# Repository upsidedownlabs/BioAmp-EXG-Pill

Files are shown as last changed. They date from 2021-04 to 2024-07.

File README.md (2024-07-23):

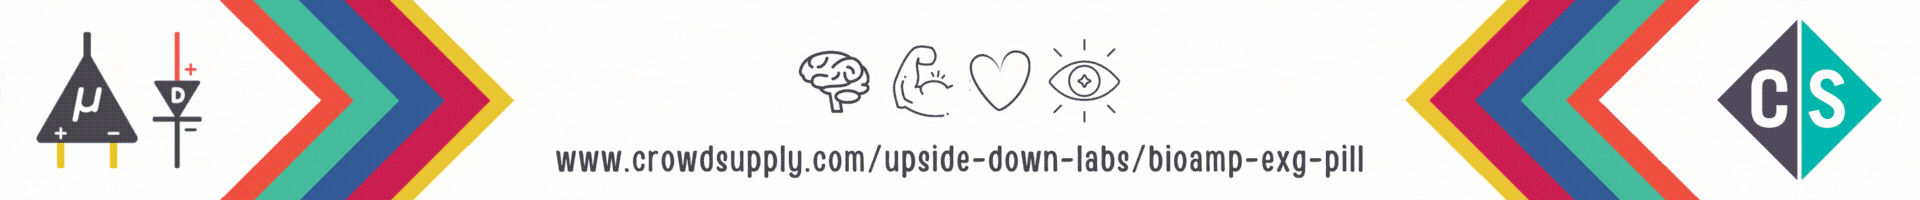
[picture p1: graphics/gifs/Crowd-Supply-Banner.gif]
Down Labs BioAmp EXG Pill Crowd Supply banner (https://www.crowdsupply.com/upside-down-labs/bioamp-exg-pill)


    

BioAmp EXG Pill is a small (2.54 X 1.00 cm) and elegant Analog Front End (AFE) board for BioPotential signal acquisition that you can use with any 5v Micro Controller Unit (MCU) with an ADC. It is capable of recording publication grade BioPotential signals like ECG, EMG, EOG, and EEG without the inclusion of any dedicated Hardware/Software filter, see [BioAmp EXG Pill v0.7 intro video](https://www.youtube.com/watch?v=-G3z9fvQnuw) for more info. The v1.0 of BioAmp EXG pill provides even more flexibilty with configuration option for Gain, BandPass, Filter, and Electrodes.

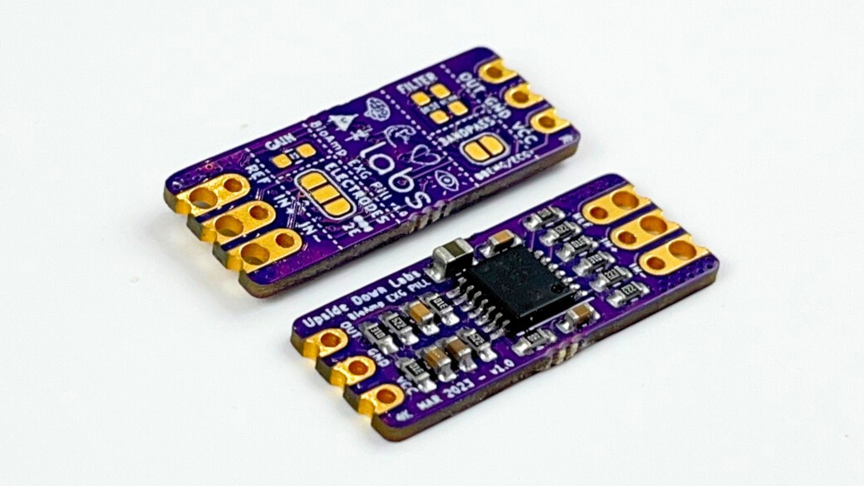
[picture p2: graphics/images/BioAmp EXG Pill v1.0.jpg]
Upside Down Labs BioAmp EXG Pill Assembled


| Connection      |  Configuration |
| :-------------------------: | :-------------------------: |
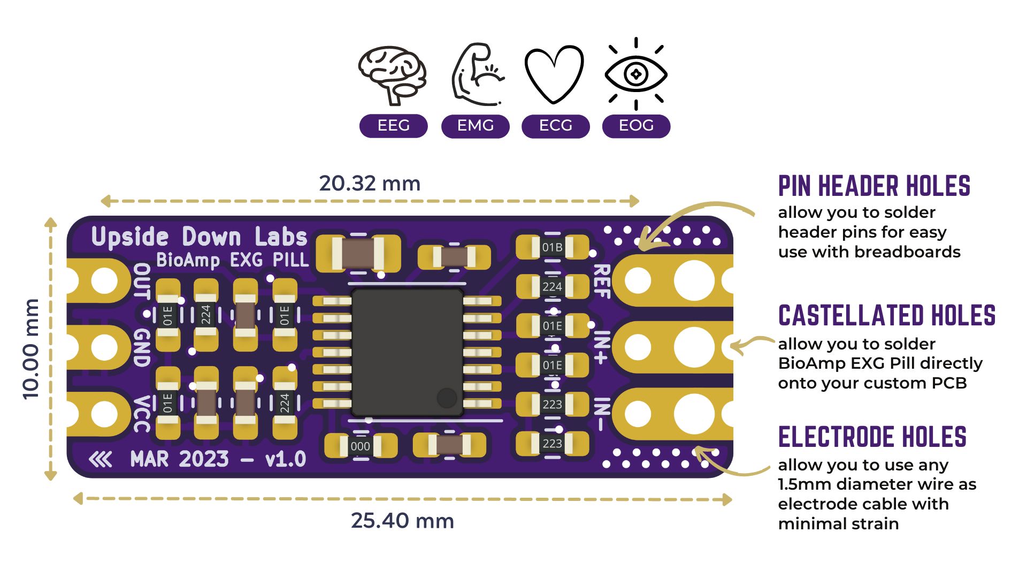
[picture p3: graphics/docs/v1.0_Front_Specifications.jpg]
BioAmp EXG Pill - Connection
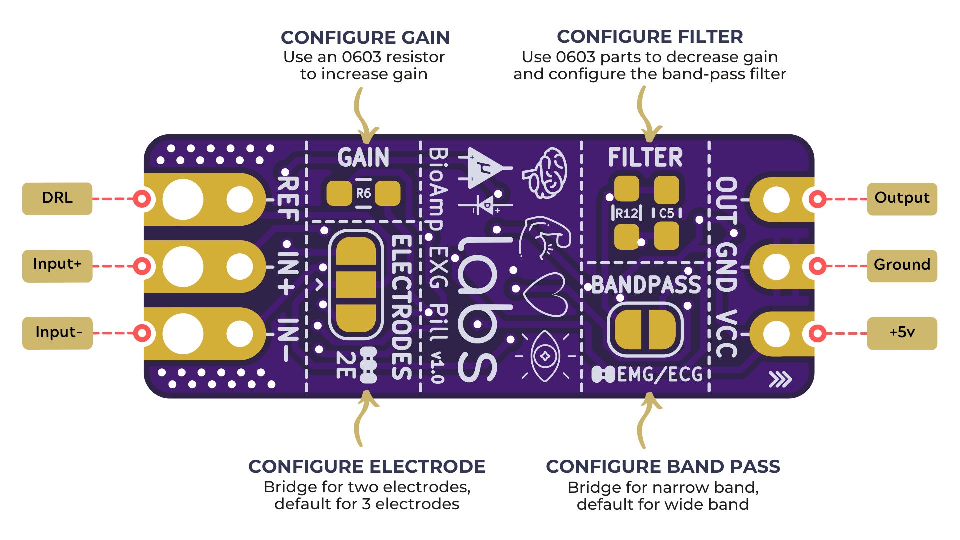
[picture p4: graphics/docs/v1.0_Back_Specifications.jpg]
BioAmp EXG Pill - Configuration
|   | |

| Basic Arduino Circuit           |  Electromyography (EMG) |
| :-------------------------: | :-------------------------: |
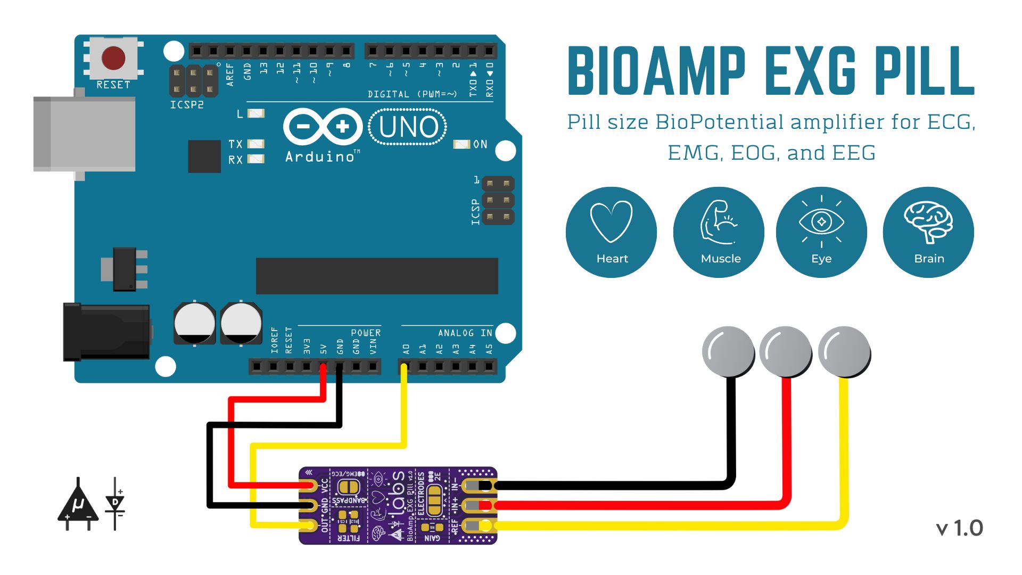
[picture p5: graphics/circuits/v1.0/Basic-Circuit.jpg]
BioAmp EXG Pill - Basic Circuit
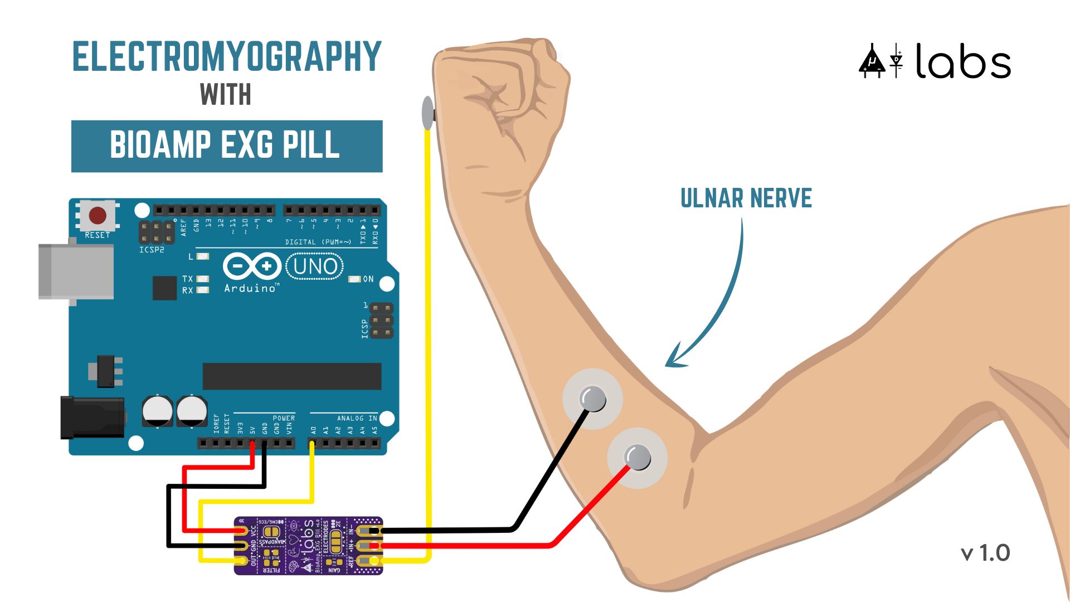
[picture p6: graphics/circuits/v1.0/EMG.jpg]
BioAmp EXG Pill - Electromyography (EMG)
|   | |

| Electrooculography (EOG) Horizontal           |  Electrooculography (EOG) Vertical |
| :-------------------------: | :-------------------------: |
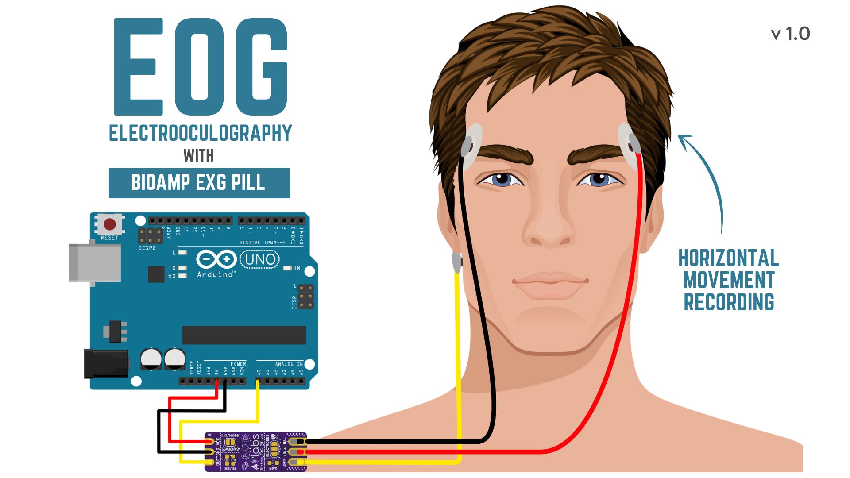
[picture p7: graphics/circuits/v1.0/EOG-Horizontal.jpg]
BioAmp EXG Pill - Electrooculography (EOG) Horizontal
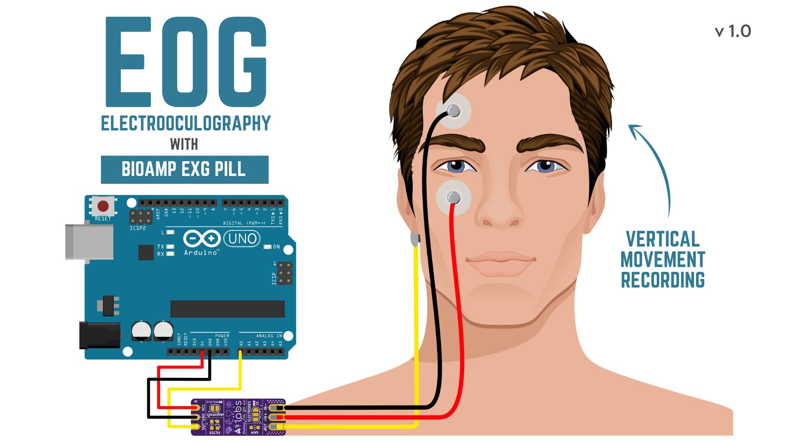
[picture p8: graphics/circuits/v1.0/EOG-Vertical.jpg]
BioAmp EXG Pill - Electrooculography (EOG) Vertical
|   | |

| Electrocardiography (ECG) Lead 1           |  Electroencephalography (EEG) |
| :-------------------------: | :-------------------------: |
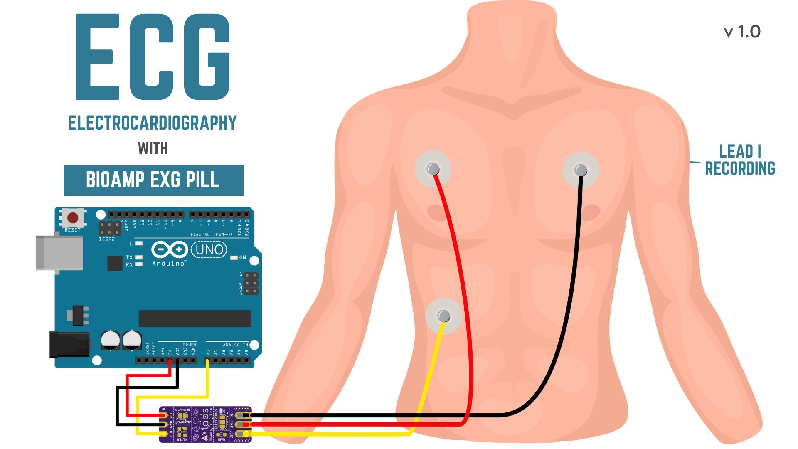
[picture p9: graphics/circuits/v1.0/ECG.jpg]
BioAmp EXG Pill - Electrocardiography (ECG) Lead 1
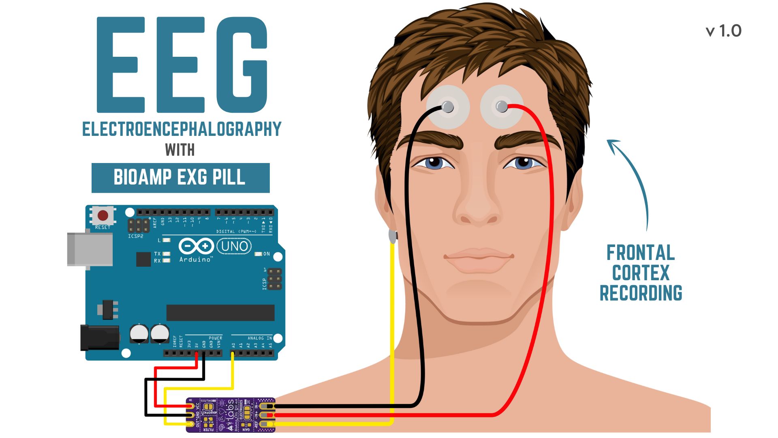
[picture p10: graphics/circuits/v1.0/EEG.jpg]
BioAmp EXG Pill - Electroencephalography (EEG)
|   | |

## Software
BioAmp EXG Pill works with any 5V microcontroller with an ADC like Arduino UNO/Nano or you can use dedicated 5v compatible ADC like ADS1115. To help with signal processing and cleaning you can use the included Arduino example sketches listed below.

| No. | Program| Description |
| ---- | ---- | ---- |
|1 | [FixedSampling](software/FixedSampling)| Sample from ADC at a fixed rate for easy processing of signal.|
|2 | [EMGFilter](software/EMGFilter)| A 74.5 - 149.5 Hz band pass filter sketch for clean Electromyography.|
|3 | [ECGFilter](software/ECGFilter)| A 0.5 - 44.5 Hz band-pass filter sketch for clean Electrocardiography.|
|4 | [EOGFilter](software/EOGFilter)| A 0.5 - 19.5 Hz band-pass filter sketch for clean Electrooculography.|
|5 | [EEGFilter](software/EEGFilter)| A 0.5 - 29.5 Hz band-pass filter sketch for clean Electroencephalography.|
|6 | [EMGEnvelop](software/EMGEnvelop)| EMG signal envelop detection for robotics and biomedical applications.|
|7 | [LEDBarGraph](software/LEDBarGraph)| LED bar graph showing EMG amplitude.|
|8 | [ServoControl](software/ServoControl)| Servo motor control with EMG.|
|9 | [HeartBeatDetection](software/HeartBeatDetection)| Standard deviation based heart beat detection algorithm.|
|10 | [EyeBlinkDetection](software/EyeBlinkDetection)|EOG based eye blink detection.|
|11 | [DrowsinessDetection](software/DrowsinessDetection)| Drowsiness detection using eye blink detection.|
|12 | [ClawController](software/ClawController)| Servo claw controller |
|13 | [EOGPhotoCaptureBLE](software/EOGPhotoCaptureBLE)| EOG based photo clicking machine using ESP32 BLE |
|14 | [Faster_HeartRateDetection](software/Faster_HeartRateDetection)| Faster and more optimzed calculation of BPM |
|15 | [OLED_BPM](software/OLED_BPM)| Display BPM values on OLED Screen|

To-Do:

| No. | Program| Description |
| ---- | ---- | ---- |
|1 | HeartRate | Heart rate calculation with ECG.|
|2 | BrainWaves | Brain waves amplitude with FFT.|
|3 | EOGController | EOG based eye movement detection (left/right) to create a game controller.|

## Hardware

BioAmp EXG Pill has been created using KiCad and all the design files can be found under [hardware](hardware/) folder, including production [Gerber](hardware/gerbers) files. Images below shows a quick overview of the hardware design.

| PCB Front           |  PCB Back |
| :-------------------------: | :-------------------------: |
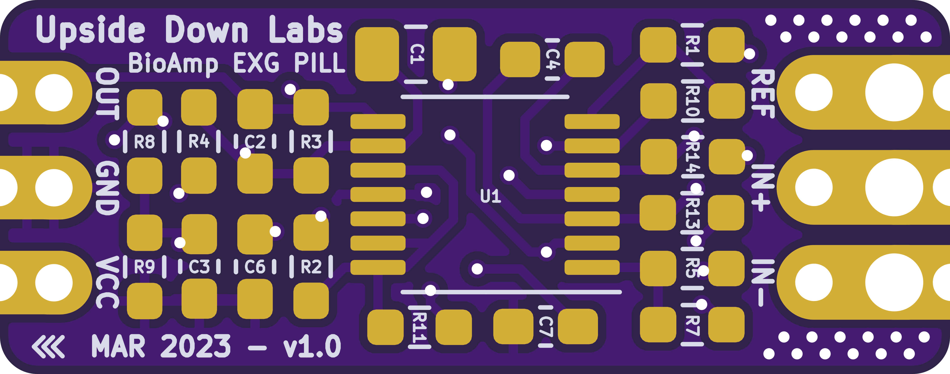
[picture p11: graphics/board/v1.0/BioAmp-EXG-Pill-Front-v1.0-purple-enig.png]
Upside Down Labs BioAmp EXG Pill front
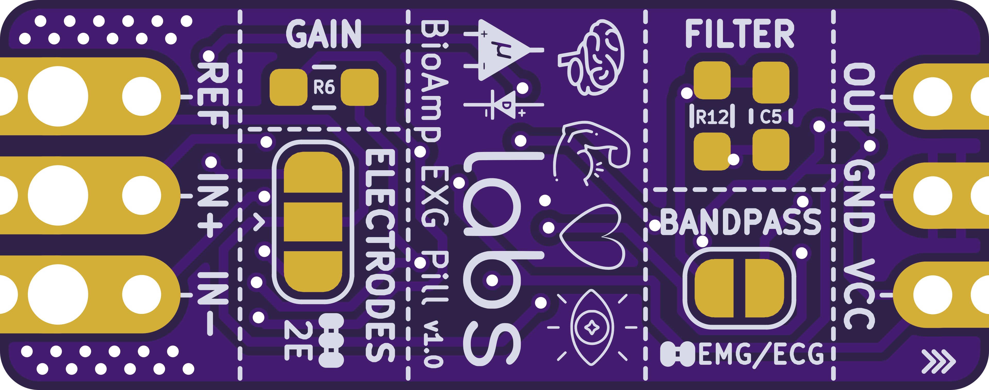
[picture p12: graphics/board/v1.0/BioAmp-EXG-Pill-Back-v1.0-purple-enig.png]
Upside Down Labs BioAmp EXG Pill back
|   |  |

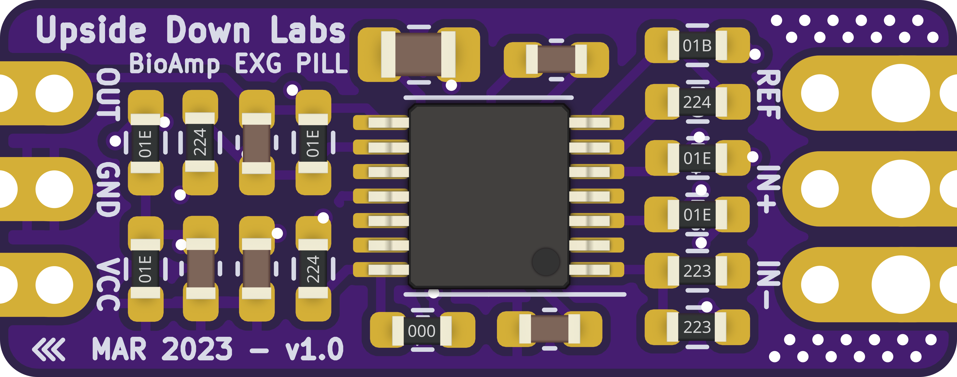
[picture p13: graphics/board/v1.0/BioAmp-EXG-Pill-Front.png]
Upside Down Labs BioAmp EXG Pill front annotated


| Dimensions            |  Schematic  |
| :-------------------------: | :-------------------------: |
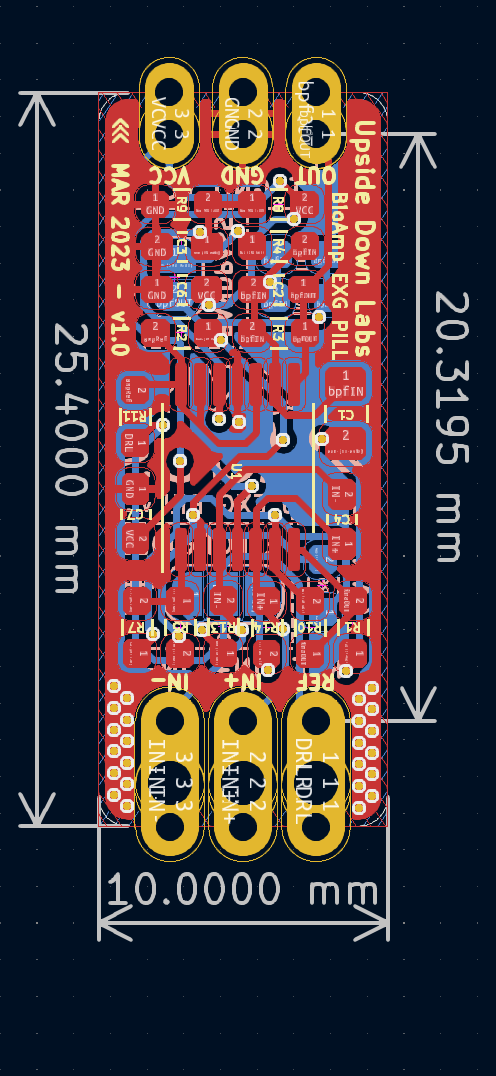
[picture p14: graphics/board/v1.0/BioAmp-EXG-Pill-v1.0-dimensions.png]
Upside Down Labs BioAmp EXG Pill dimensions
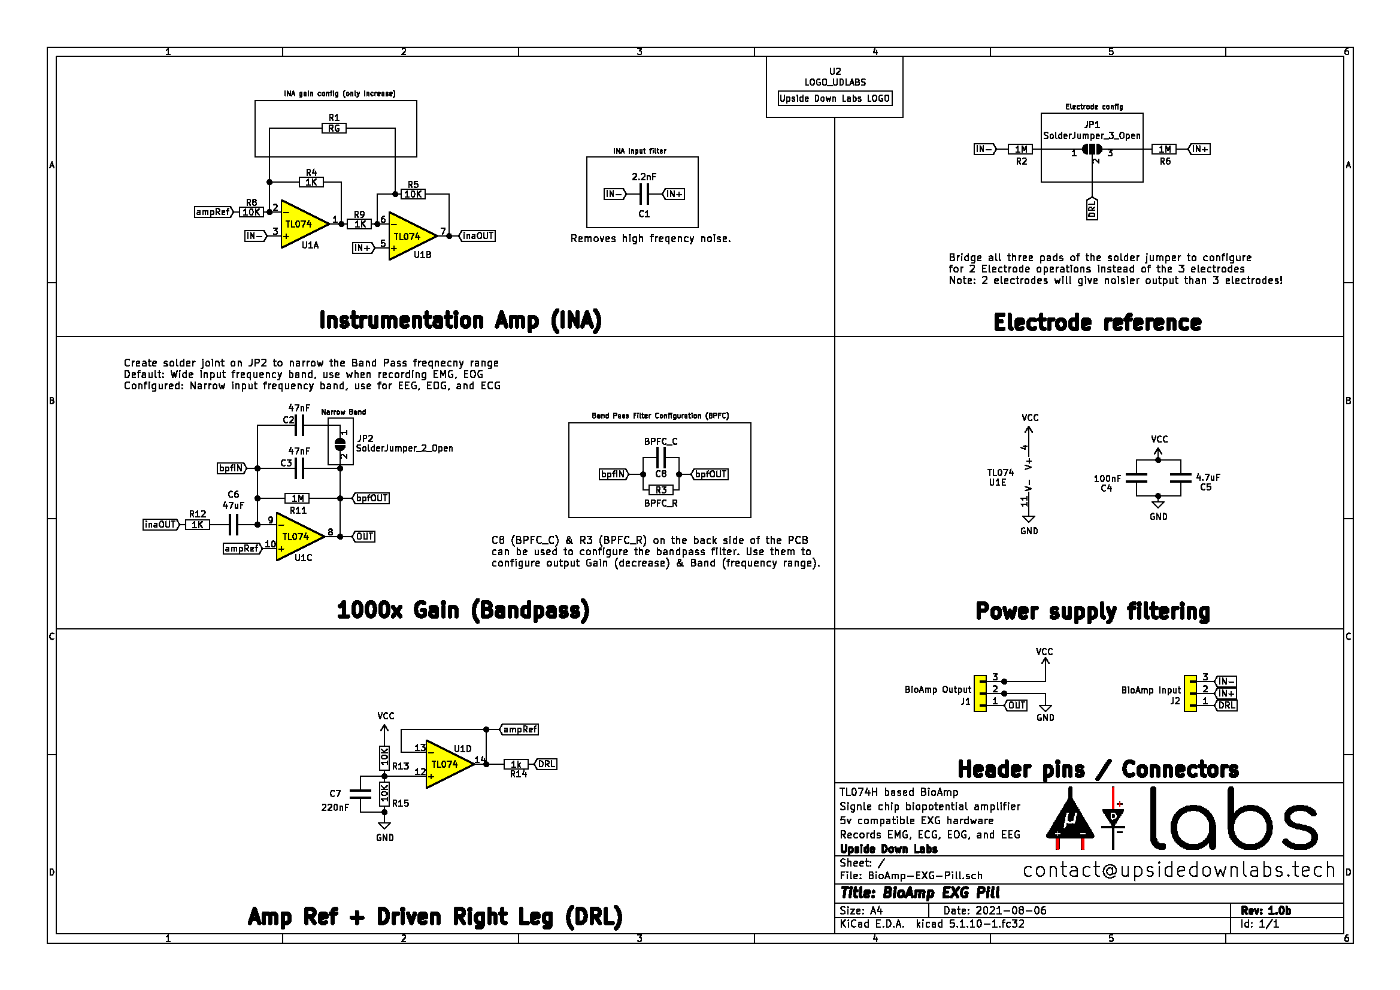
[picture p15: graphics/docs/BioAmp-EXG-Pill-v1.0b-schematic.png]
Upside Down Labs BioAmp EXG Pill schematic
|   |  |

## License

| Licenses Facts              |  OSHWA Certification |
| :-------------------------: | :-------------------------: |
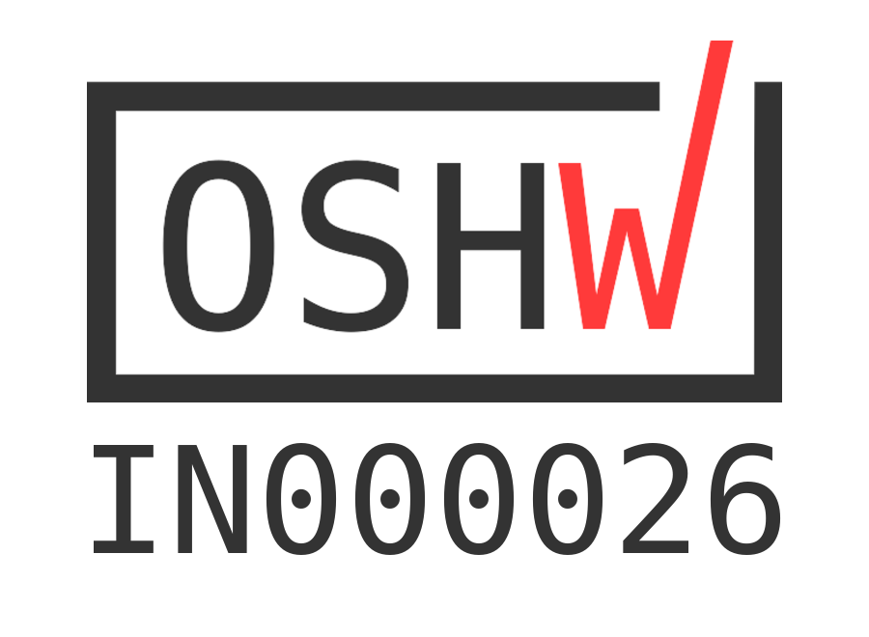
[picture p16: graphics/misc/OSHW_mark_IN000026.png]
Open Source Hardware Certification mark
| <a href="LICENSE.md">Open Source Licenses Facts</a>  |  |

#### Hardware
CERN Open Hardware License Version 2 - Strongly Reciprocal ([CERN-OHL-S-2.0](https://spdx.org/licenses/CERN-OHL-S-2.0.html)).

#### Software
MIT open source [license](http://opensource.org/licenses/MIT).

#### Documentation:
<br />This work is licensed under a <a rel="license" href="http://creativecommons.org/licenses/by/4.0/">Creative Commons Attribution 4.0 International License</a>.

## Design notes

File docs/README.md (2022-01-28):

<br/>
<br/>

Down Labs BioAmp EXG Pill Crowd Supply banner

     

BioAmp EXG Pill is a small (2.54 X 1.00 cm) and elegant Analog Front End (AFE) board for BioPotential signal acquisition that you can use with any 5v Micro Controller Unit (MCU) with an ADC. It is capable of recording publication grade BioPotential signals like ECG, EMG, EOG, and EEG without the inclusion of any dedicated Hardware/Software filter, see [BioAmp EXG Pill v0.7 intro video](https://www.youtube.com/watch?v=-G3z9fvQnuw) for more info. The v1.0 of BioAmp EXG pill provides even more flexibilty with configuration option for Gain, BandPass, Filter, and Electrodes.

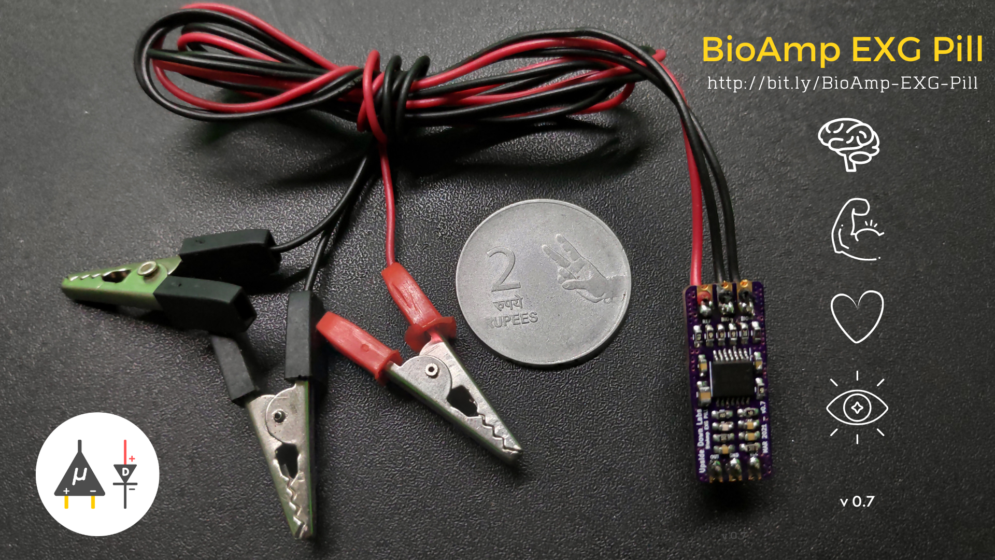
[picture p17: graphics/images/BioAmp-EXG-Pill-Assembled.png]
Upside Down Labs BioAmp EXG Pill Assembled


| Connection      |  Configuration |
| :-------------------------: | :-------------------------: |
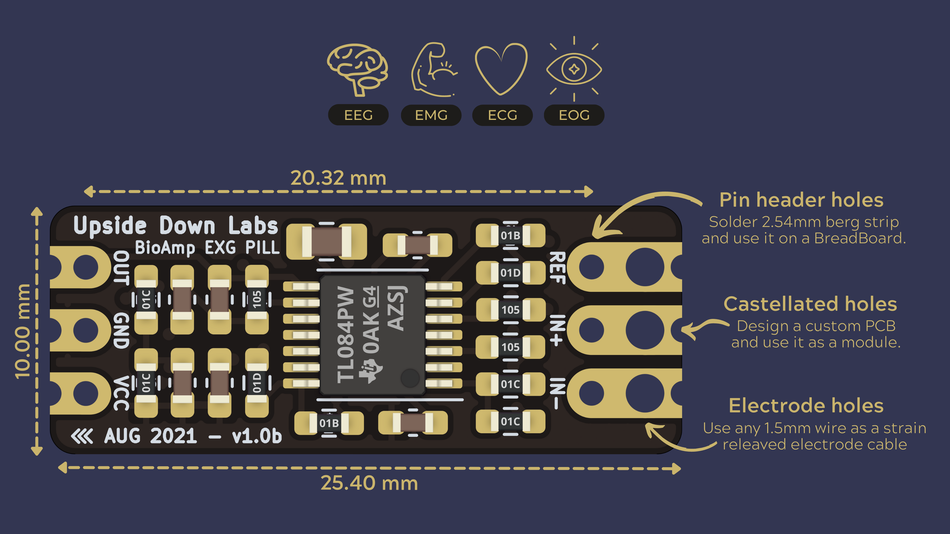
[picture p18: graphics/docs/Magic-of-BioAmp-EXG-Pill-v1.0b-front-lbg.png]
BioAmp EXG Pill - Connection
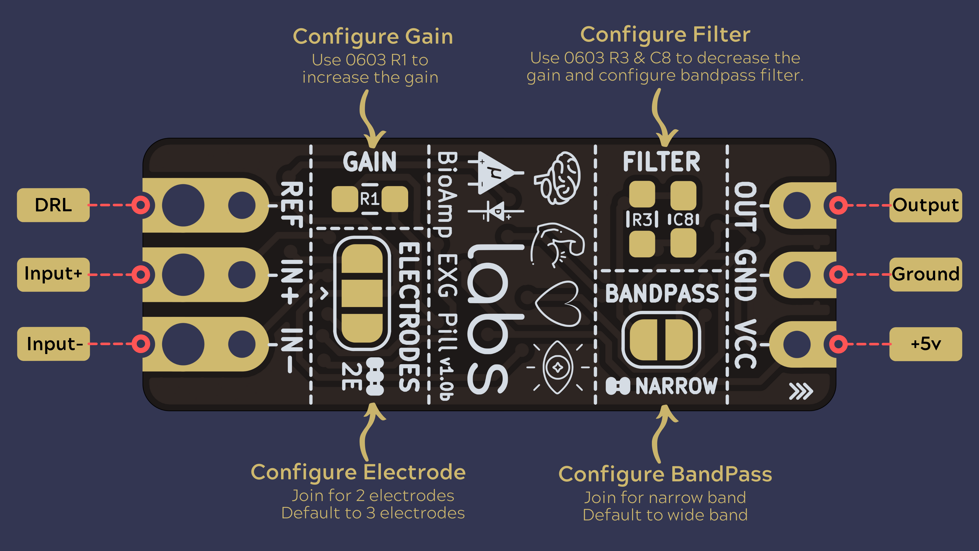
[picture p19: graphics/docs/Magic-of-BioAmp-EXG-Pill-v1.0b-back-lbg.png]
BioAmp EXG Pill - Configuration
|   | |

| Basic Arduino Circuit           |  Electromyography (EMG) |
| :-------------------------: | :-------------------------: |
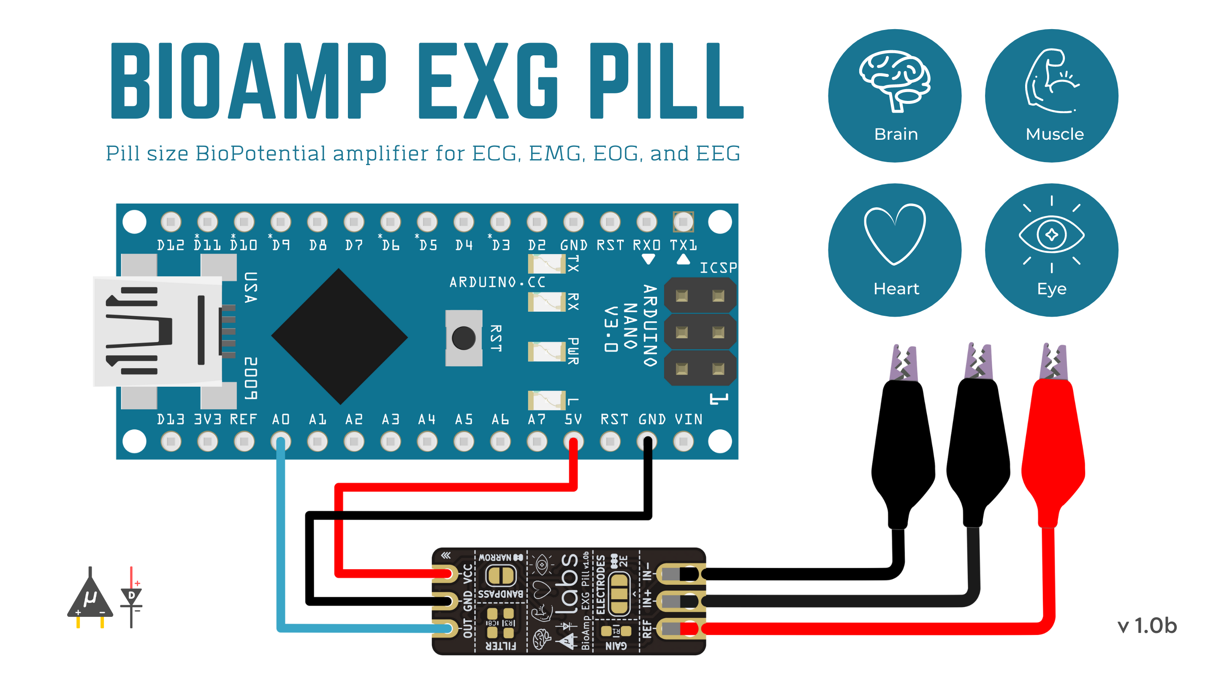
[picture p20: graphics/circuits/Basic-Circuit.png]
BioAmp EXG Pill - Basic Circuit
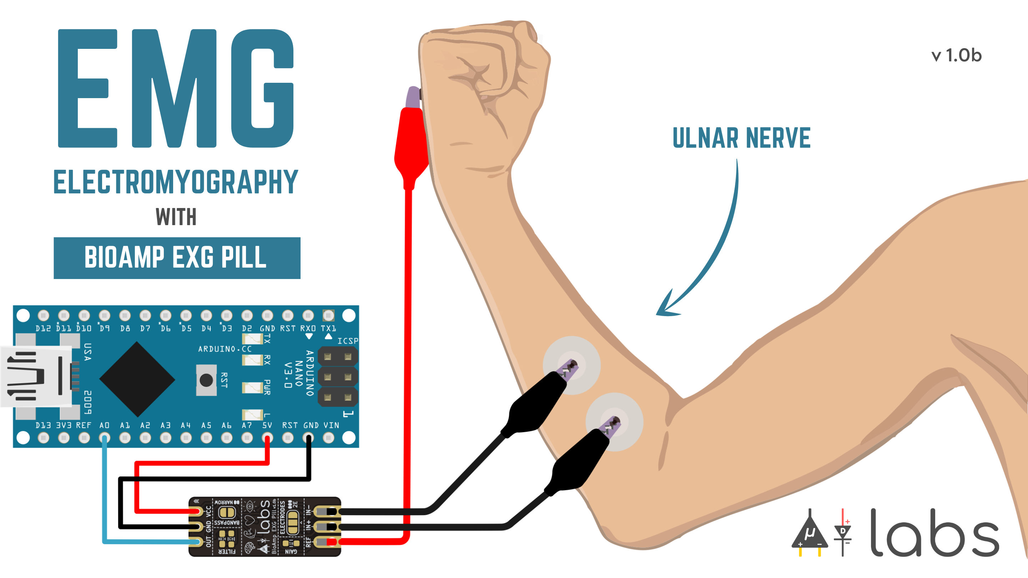
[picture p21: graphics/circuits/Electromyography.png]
BioAmp EXG Pill - Electromyography (EMG)
|   | |

| Electrooculography (EOG) Horizontal           |  Electrooculography (EOG) Vertical |
| :-------------------------: | :-------------------------: |
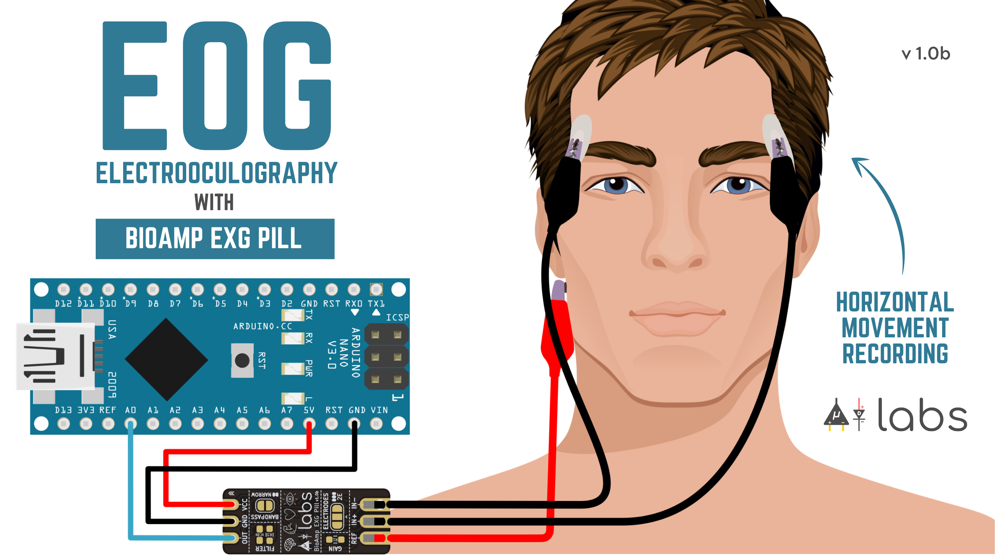
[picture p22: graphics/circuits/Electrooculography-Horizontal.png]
BioAmp EXG Pill - Electrooculography (EOG) Horizontal
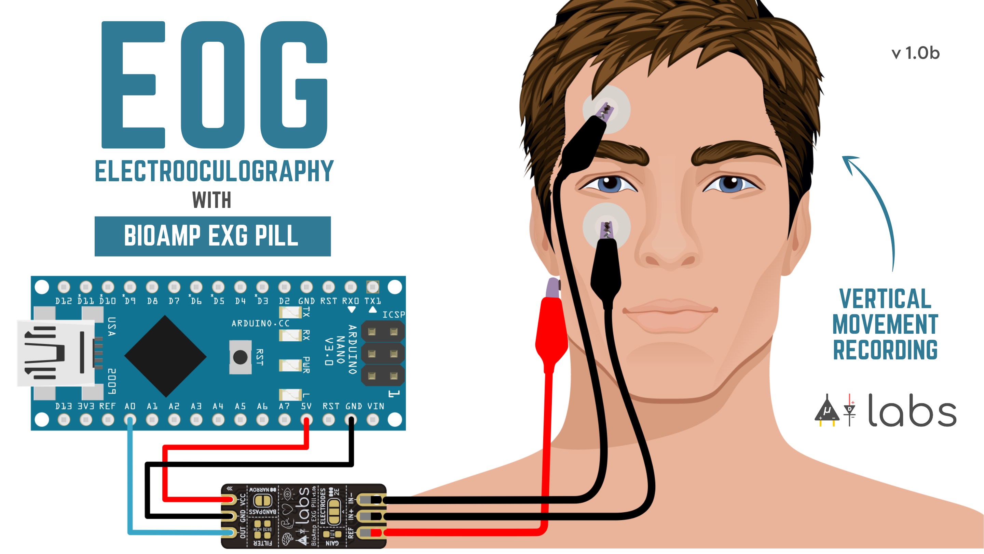
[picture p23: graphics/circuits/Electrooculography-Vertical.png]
BioAmp EXG Pill - Electrooculography (EOG) Vertical
|   | |

| Electrocardiography (ECG) Lead 1           |  Electroencephalography (EEG) |
| :-------------------------: | :-------------------------: |
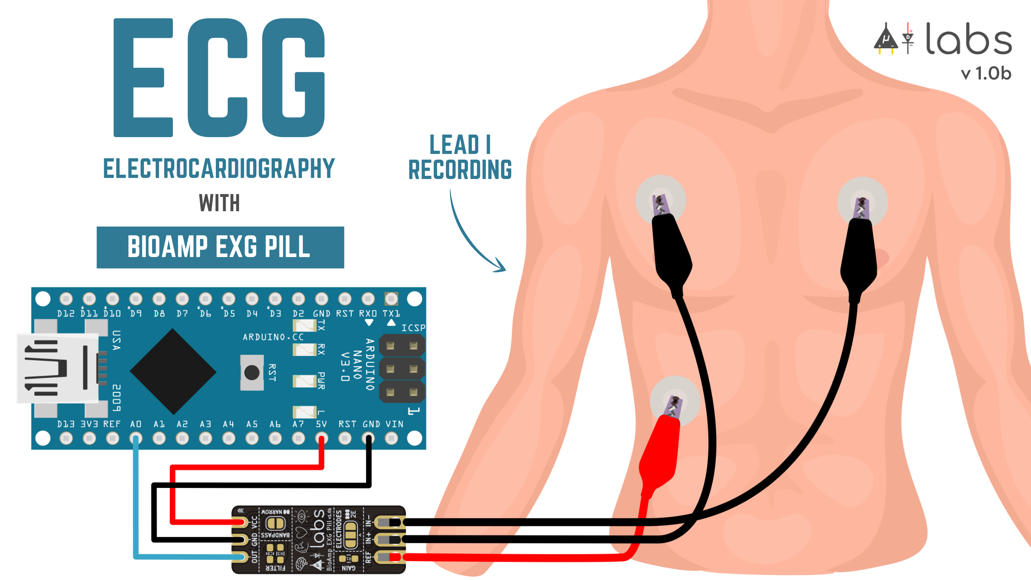
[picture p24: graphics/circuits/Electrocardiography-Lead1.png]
BioAmp EXG Pill - Electrocardiography (ECG) Lead 1
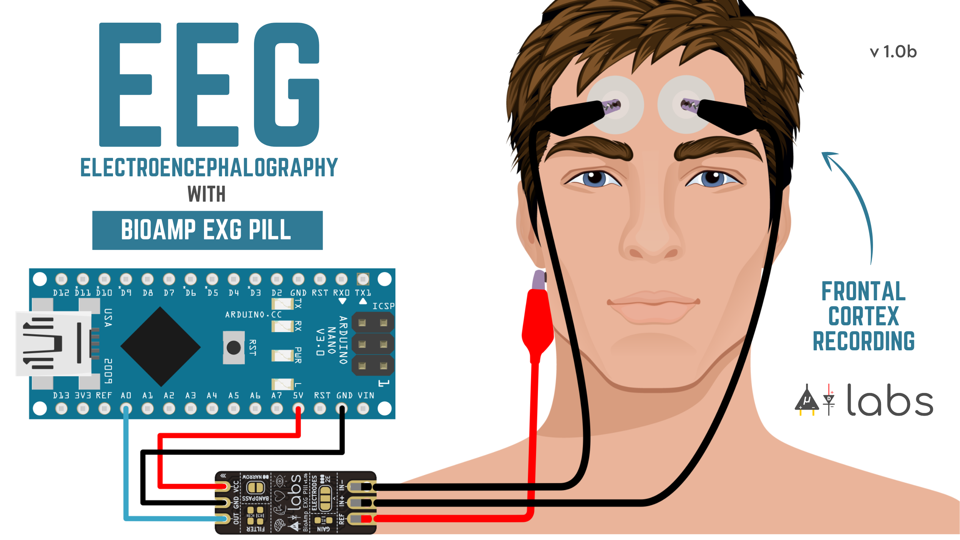
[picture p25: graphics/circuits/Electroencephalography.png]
BioAmp EXG Pill - Electroencephalography (EEG)
|   | |

## Software
BioAmp EXG Pill works with any 5V microcontroller with an ADC like Arduino UNO/Nano or you can use dedicated 5v compatible ADC like ADS1115. To help with signal processing and cleaning you can use the included Arduino example sketches listed below.

| No. | Program| Description |
| ---- | ---- | ---- |
|1 | [FixedSampling](software/FixedSampling)| Sample from ADC at a fixed rate for easy processing of signal.|
|2 | [EMGFilter](software/EMGFilter)| A 74.5 - 149.5 Hz band pass filter sketch for clean Electromyography.|
|3 | [ECGFilter](software/ECGFilter)| A 0.5 - 44.5 Hz band-pass filter sketch for clean Electrocardiography.|
|4 | [EOGFilter](software/EOGFilter)| A 0.5 - 19.5 Hz band-pass filter sketch for clean Electrooculography.|
|5 | [EEGFilter](software/EEGFilter)| A 0.5 - 29.5 Hz band-pass filter sketch for clean Electroencephalography.|
|6 | [EMGEnvelop](software/EMGEnvelop)| EMG signal envelop detection for robotics and biomedical applications.|
|7 | [LEDBarGraph](software/LEDBarGraph)| LED bar graph showing EMG amplitude.|
|8 | [ServoControl](software/ServoControl)| Servo motor control with EMG.|
|9 | [HeartBeatDetection](software/HeartBeatDetection)| Standard deviation based heart beat detection algorithm.|
|10 | [EyeBlinkDetection](software/EyeBlinkDetection)|EOG based eye blink detection.|
|11 | [DrowsinessDetection](software/DrowsinessDetection)| Drowsiness detection using eye blink detection.|
|12 | [ClawController](software/ClawController)| Servo claw controller |
|13 | [EOGPhotoCaptureBLE](software/EOGPhotoCaptureBLE)| EOG based photo clicking machine using ESP32 BLE |

To-Do:

| No. | Program| Description |
| ---- | ---- | ---- |
|1 | BrainWaves | Brain waves amplitude with FFT.|
|2 | EOGController | EOG based eye movement detection (left/right) to create a game controller.|

## Hardware

BioAmp EXG Pill has been created using KiCad and all the design files can be found under [hardware](hardware/) folder, including production [Gerber](hardware/gerbers) files. Images below shows a quick overview of the hardware design.

| PCB Front           |  PCB Back |
| :-------------------------: | :-------------------------: |
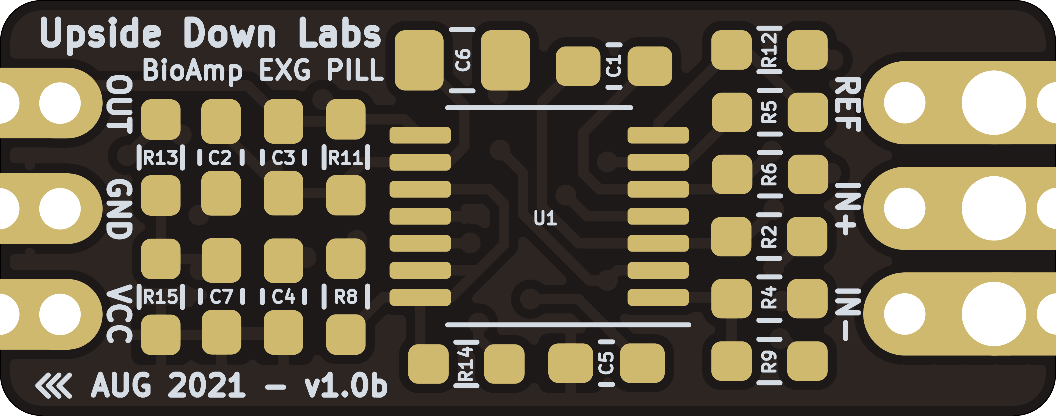
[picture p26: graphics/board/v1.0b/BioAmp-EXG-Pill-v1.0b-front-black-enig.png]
Upside Down Labs BioAmp EXG Pill front
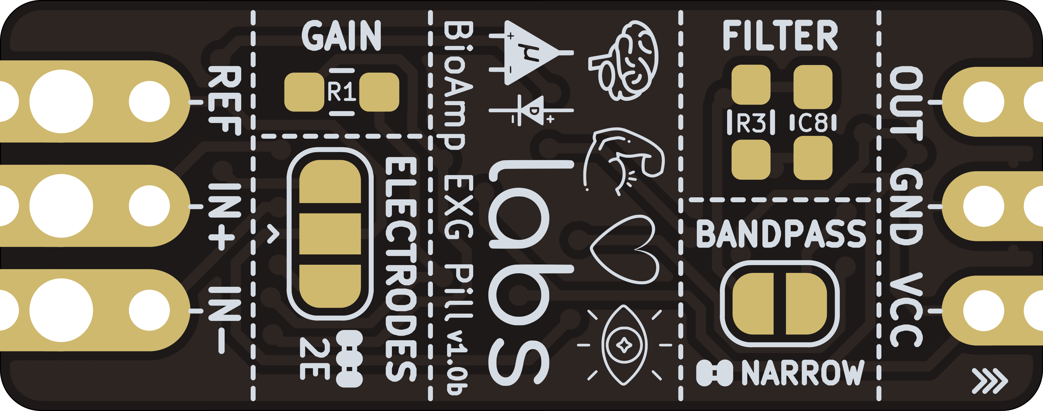
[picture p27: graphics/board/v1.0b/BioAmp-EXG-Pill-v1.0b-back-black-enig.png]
Upside Down Labs BioAmp EXG Pill back
|   |  |

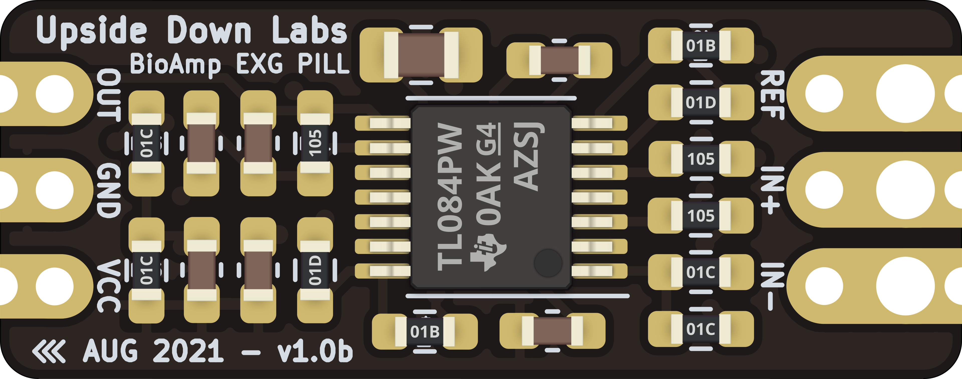
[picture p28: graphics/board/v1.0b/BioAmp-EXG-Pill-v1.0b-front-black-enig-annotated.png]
Upside Down Labs BioAmp EXG Pill front annotated


| Dimensions            |  Schematic  |
| :-------------------------: | :-------------------------: |
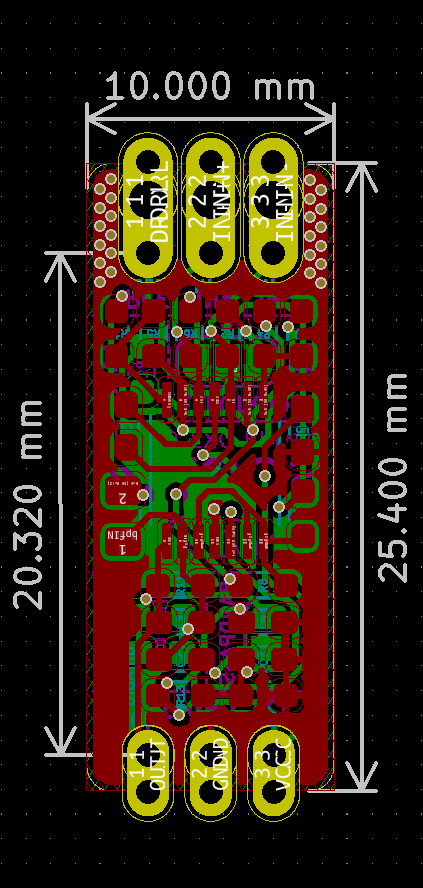
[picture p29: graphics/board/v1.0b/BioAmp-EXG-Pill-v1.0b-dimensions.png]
Upside Down Labs BioAmp EXG Pill dimensions
|   | Upside Down Labs BioAmp EXG Pill schematic |

## License

| Licenses Facts              |  OSHWA Certification |
| :-------------------------: | :-------------------------: |
| <a href="LICENSE.md">Open Source Licenses Facts</a>  | <a href="https://certification.oshwa.org/in000026.html">Open Source Hardware Certification mark</a> |

#### Hardware
CERN Open Hardware License Version 2 - Strongly Reciprocal ([CERN-OHL-S-2.0](https://spdx.org/licenses/CERN-OHL-S-2.0.html)).

#### Software
MIT open source [license](http://opensource.org/licenses/MIT).

#### Documentation:
<br />This work is licensed under a <a rel="license" href="http://creativecommons.org/licenses/by/4.0/">Creative Commons Attribution 4.0 International License</a>.

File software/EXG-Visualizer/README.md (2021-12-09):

# ESP32 oscilloscope with Web user interface - see the signals the way ESP32 sees them

## Demo
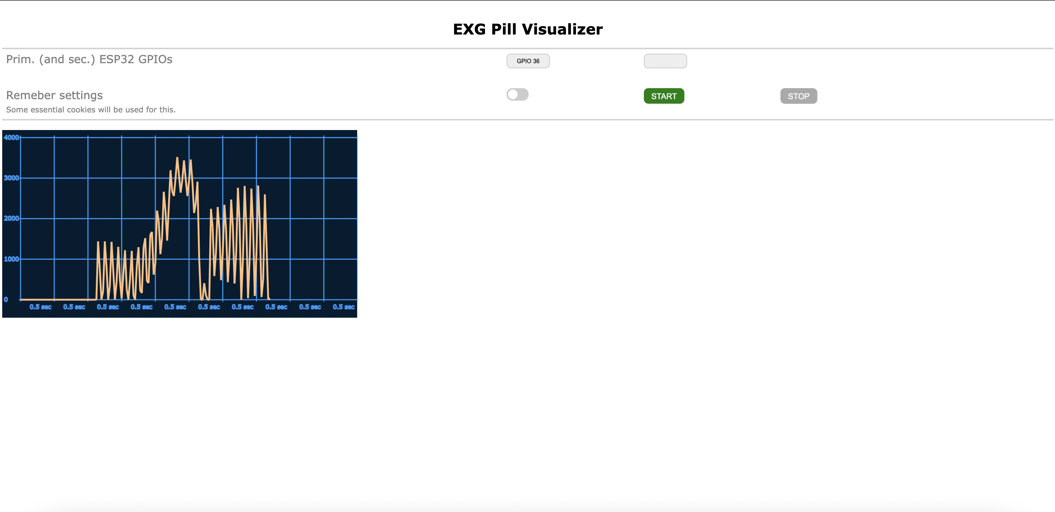
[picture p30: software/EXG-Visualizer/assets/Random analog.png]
image info


## Setup instructions

1. Copy all files in this package into EXG-Visulizer directory.
2. Open EXG-Visualizer.ino with Arduino IDE.
3. Find and change YOUR-STA-SSID to your WiFi SSID and YOUR-STA-PASSWORD to your WiFi password.
4. In your Arduino IDE under Tools|Board make sure you choose "ESP32 Dev Module" or a board allowing partition schemes
5. Visualizer uses FAT file system so select one of FATFS partition schemas (Arduino IDE under Tools|Partition Scheme|...)
6. Compile sketch and run it on your ESP32 for the first time. Doing this, ESP32 flash memory will be formatted with FAT file system. WARNING: every information you have stored into ESP32�s flash memory will be lost.
7. FTP to your ESP32 (By using ftp command line utility or Windows explorer. User name and password are not required) and upload the following files into /var/www/html directory:

   - android-192-osc.png,
   - apple-180-osc.png,
   - oscilloscope.html.
  
   You can find the ftp IP in the serial monitor.
```
C:\EXG-Visualizer>ftp YOUR-ESP32-IP
Connected to 10.0.0.3.
220-ESP32 FTP server - everyone is allowed to login
User (10.0.0.3:(none)):
331 enter password
Password:
230 logged on, use "/" to refer to your home directory "/"
ftp> put android-192-osc.png /var/www/html/android-192.png
226 /var/www/html/android-192-osc.png transfer complete
ftp> put apple-180-osc.png /var/www/html/apple-180.png
226 /var/www/html/apple-180-osc.png transfer complete
ftp> put oscilloscope.html /var/www/html/oscilloscope.html
226 /var/www/html/visualizer.html transfer complete
ftp> ls
200 port ok
150 starting transfer
-r-xr-xrwx   1 owner    group            1818 Aug 24 10:47      /var/www/html/android-192-osc.png
-r-xr-xrwx   1 owner    group            1596 Aug 24 10:47      /var/www/html/apple-180-osc.png
-r-xr-xrwx   1 owner    group           39515 Aug 24 10:47      /var/www/html/visualizer.html
226 transfer complete
ftp>
```

8. Open http://YOUR-ESP32-IP/oscilloscope.html with your browser.

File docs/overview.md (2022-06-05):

<!---
BioAmp EXG Pill is a small (2.54 X 1.00 cm) and elegant Analog Front End (AFE) board for BioPotential signal acquisition that you can use with any 5v Micro Controller Unit (MCU) with an ADC. It is capable of recording publication grade BioPotential signals like ECG, EMG, EOG, and EEG without the inclusion of any dedicated Hardware/Software filter, see [BioAmp EXG Pill v0.7 intro video](https://www.youtube.com/watch?v=-G3z9fvQnuw) for more info. The v1.0 of BioAmp EXG pill provides even more flexibilty with configuration option for Gain, BandPass, Filter, and Electrodes.

![Upside Down Labs BioAmp EXG Pill Assembled](graphics/images/BioAmp-EXG-Pill-Assembled.png)

| Connection      |  Configuration |
| :-------------------------: | :-------------------------: |
| ![BioAmp EXG Pill - Connection](graphics/docs/Magic-of-BioAmp-EXG-Pill-v1.0b-front-lbg.png)  | ![BioAmp EXG Pill - Configuration](graphics/docs/Magic-of-BioAmp-EXG-Pill-v1.0b-back-lbg.png)|

| Basic Arduino Circuit           |  Electromyography (EMG) |
| :-------------------------: | :-------------------------: |
| ![BioAmp EXG Pill - Basic Circuit](graphics/circuits/Basic-Circuit.png)  | ![BioAmp EXG Pill - Electromyography (EMG)](graphics/circuits/Electromyography.png)|

| Electrooculography (EOG) Horizontal           |  Electrooculography (EOG) Vertical |
| :-------------------------: | :-------------------------: |
| ![BioAmp EXG Pill - Electrooculography (EOG) Horizontal](graphics/circuits/Electrooculography-Horizontal.png)  | ![BioAmp EXG Pill - Electrooculography (EOG) Vertical](graphics/circuits/Electrooculography-Vertical.png)|

| Electrocardiography (ECG) Lead 1           |  Electroencephalography (EEG) |
| :-------------------------: | :-------------------------: |
| ![BioAmp EXG Pill - Electrocardiography (ECG) Lead 1](graphics/circuits/Electrocardiography-Lead1.png)  | ![BioAmp EXG Pill - Electroencephalography (EEG)](graphics/circuits/Electroencephalography.png)|

## Software
BioAmp EXG Pill works with any 5V microcontroller with an ADC like Arduino UNO/Nano or you can use dedicated 5v compatible ADC like ADS1115. To help with signal processing and cleaning you can use the included Arduino example sketches listed below.

| No. | Program| Description |
| ---- | ---- | ---- |
|1 | [FixedSampling](software/FixedSampling)| Sample from ADC at a fixed rate for easy processing of signal.|
|2 | [EMGFilter](software/EMGFilter)| A 74.5 - 149.5 Hz band pass filter sketch for clean Electromyography.|
|3 | [ECGFilter](software/ECGFilter)| A 0.5 - 44.5 Hz band-pass filter sketch for clean Electrocardiography.|
|4 | [EOGFilter](software/EOGFilter)| A 0.5 - 19.5 Hz band-pass filter sketch for clean Electrooculography.|
|5 | [EEGFilter](software/EEGFilter)| A 0.5 - 29.5 Hz band-pass filter sketch for clean Electroencephalography.|
|6 | [EMGEnvelop](software/EMGEnvelop)| EMG signal envelop detection for robotics and biomedical applications.|
|7 | [LEDBarGraph](software/LEDBarGraph)| LED bar graph showing EMG amplitude.|
|8 | [ServoControl](software/ServoControl)| Servo motor control with EMG.|
|9 | [HeartBeatDetection](software/HeartBeatDetection)| Standard deviation based heart beat detection algorithm.|
|10 | [EyeBlinkDetection](software/EyeBlinkDetection)|EOG based eye blink detection.|
|11 | [DrowsinessDetection](software/DrowsinessDetection)| Drowsiness detection using eye blink detection.|
|12 | [ClawController](software/ClawController)| Servo claw controller |
|13 | [EOGPhotoCaptureBLE](software/EOGPhotoCaptureBLE)| EOG based photo clicking machine using ESP32 BLE |

To-Do:

| No. | Program| Description |
| ---- | ---- | ---- |
|1 | HeartRate | Heart rate calculation with ECG.|
|2 | BrainWaves | Brain waves amplitude with FFT.|
|3 | EOGController | EOG based eye movement detection (left/right) to create a game controller.|

## Hardware

BioAmp EXG Pill has been created using KiCad and all the design files can be found under [hardware](hardware/) folder, including production [Gerber](hardware/gerbers) files. Images below shows a quick overview of the hardware design.

| PCB Front           |  PCB Back |
| :-------------------------: | :-------------------------: |
| ![Upside Down Labs BioAmp EXG Pill front](graphics/board/v1.0b/BioAmp-EXG-Pill-v1.0b-front-black-enig.png)  | ![Upside Down Labs BioAmp EXG Pill back](graphics/board/v1.0b/BioAmp-EXG-Pill-v1.0b-back-black-enig.png) |

![Upside Down Labs BioAmp EXG Pill front annotated](graphics/board/v1.0b/BioAmp-EXG-Pill-v1.0b-front-black-enig-annotated.png)

| Dimensions            |  Schematic  |
| :-------------------------: | :-------------------------: |
| ![Upside Down Labs BioAmp EXG Pill dimensions](graphics/board/v1.0b/BioAmp-EXG-Pill-v1.0b-dimensions.png)  | ![Upside Down Labs BioAmp EXG Pill schematic](graphics/docs/BioAmp-EXG-Pill-v1.0b-schematic.png) |

## License

| Licenses Facts              |  OSHWA Certification |
| :-------------------------: | :-------------------------: |
| <a href="LICENSE.md"><img src="graphics/misc/Licenses_facts.svg" width="400" alt="Open Source Licenses Facts"/></a>  | <a href="https://certification.oshwa.org/in000026.html"><img src="graphics/misc/OSHW_mark_IN000026.png" width="300" alt="Open Source Hardware Certification mark"/></a> |

#### Hardware
CERN Open Hardware License Version 2 - Strongly Reciprocal ([CERN-OHL-S-2.0](https://spdx.org/licenses/CERN-OHL-S-2.0.html)).

#### Software
MIT open source [license](http://opensource.org/licenses/MIT).

#### Documentation:
<a rel="license" href="http://creativecommons.org/licenses/by/4.0/"><img alt="Creative Commons License" style="border-width:0" src="https://i.creativecommons.org/l/by/4.0/88x31.png" /></a><br />This work is licensed under a <a rel="license" href="http://creativecommons.org/licenses/by/4.0/">Creative Commons Attribution 4.0 International License</a>.
--->

This page will describe overview of Bio-Amp-EXG-pill.

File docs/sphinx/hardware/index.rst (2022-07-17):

Hardware
========

1. :ref:`Arduino <open10>`
2. :ref:`ESP32 <open11>`
3. :ref:`RPi Pico <open12>`
4. :ref:`STM32 <open13>`
5. :ref:`BBBW <open14>`

|

.. _open10:

Arduino
*******

This section will contain info about using Bio-Amp-EXG-Pill with arduino.

|

.. _open11:

ESP32
******

This section will contain info about using Bio-Amp-EXG-Pill with ESP32.

|

.. _open12:

RPi Pico 
*********

This section will contain info about using Bio-Amp-EXG-Pill with RPi Pico.

|

.. _open13:

STM32
******

This section will contain info about using Bio-Amp-EXG-Pill with STM32 Blue Pill.

|

.. _open14:

BBBW
*****

This section will contain info about using Bio-Amp-EXG-Pill with bbbw board.

|

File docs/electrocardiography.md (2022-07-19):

## Electrocardiography (ECG) &#10084;

We are delighted to share that BioAmp EXG Pill is among the top ten <a href="https://hackaday.com/2021/08/31/ten-winners-of-the-hackaday-prize-supportive-tech-challenge/" style="color: Red; text-decoration: none;"> Winners Of The Hackaday Prize Supportive Tech Challenge </a>. It was all possible because of various <a href="https://github.com/upsidedownlabs/BioAmp-EXG-Pill/tree/main/software" style="color: Red; text-decoration: none;"> Arduino example sketches</a>  and projects that are available for the BioAmp EXG Pill which you can use to create a supportive technology. For example, you can create a mobile heart ailment detection machine, prosthetic hand controller, EOG-based game controller, and many more similar projects. Let’s take a look at how you can use BioAmp EXG Pill to detect heartbeats and potentially create a real-time heart monitor.

## Detecting heartbeats with BioAmp EXG Pill & Arduino Nano

An accurate heartbeat detection (peak detection) algorithm that works on a small microcontroller is a pretty complex task but, with our robust standard deviation-based peak detection algorithm, you can detect heartbeats very easily even on an Arduino Nano.

<br>

<p style="text-align: center;"> <b>Resulting ECG Signal Wave</b></p>

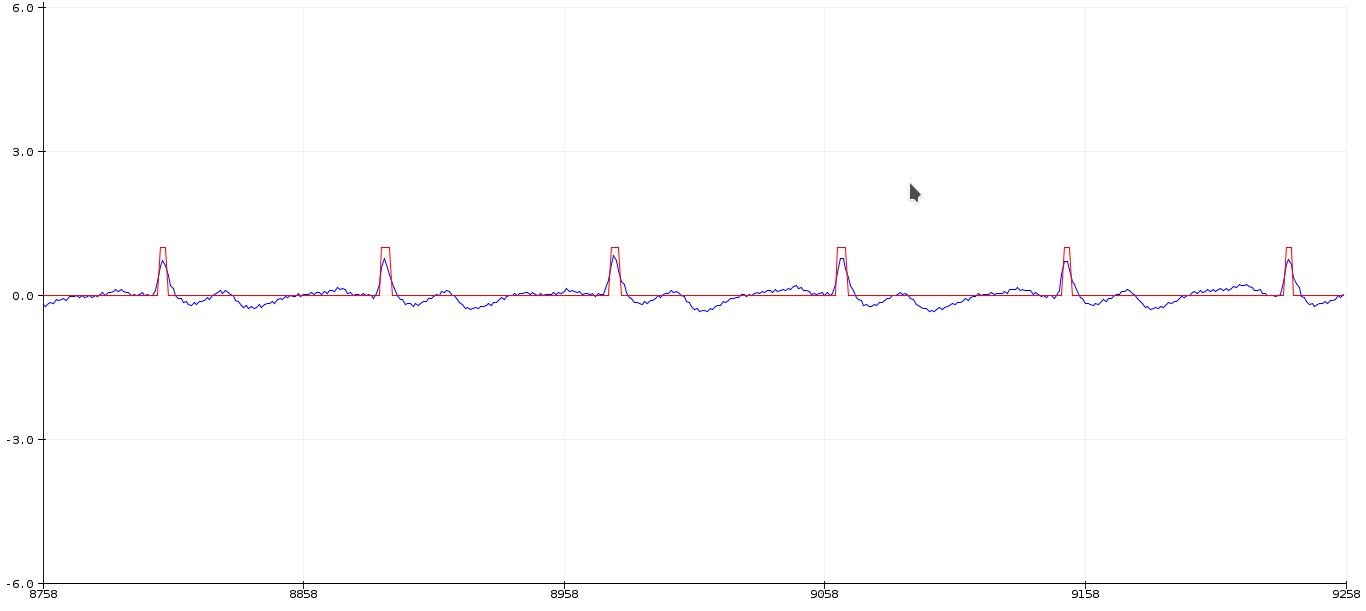
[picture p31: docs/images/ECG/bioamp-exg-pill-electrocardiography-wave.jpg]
ecg-wave-diagram


To record ECG and detect a heartbeat in that ECG on an Arduino Nano you first need to flash the <a href="https://github.com/upsidedownlabs/BioAmp-EXG-Pill/blob/main/software/HeartBeatDetection/HeartBeatDetection.ino" style="color: Red; text-decoration: none;">Heart Beat Detection Arduino sketch</a> onto your Nano and then connect the electrodes either on your chest or hands.  

_**Note:** BioAmp EXG Pill is not a certified medical device and shouldn't be treated like one._
<br><br>

- ### Chest ECG heartbeat detection

A very basic method for detecting heartbeats is to place the electrodes near the heart, as shown below. You just have to flash the <a href="https://github.com/upsidedownlabs/BioAmp-EXG-Pill/blob/main/software/HeartBeatDetection/HeartBeatDetection.ino" style="color: Red; text-decoration: none;"> Heart Beat Detection Arduino sketch </a>  to your Nano, do the wiring, and connect the electrodes like this:

1. IN- near LEFT shoulder
2. IN+ near RIGHT shoulder
3. REF above Right leg

<br>

<p style="text-align: center;"> <b> Wiring and Electrode placement for chest ECG</b></p>

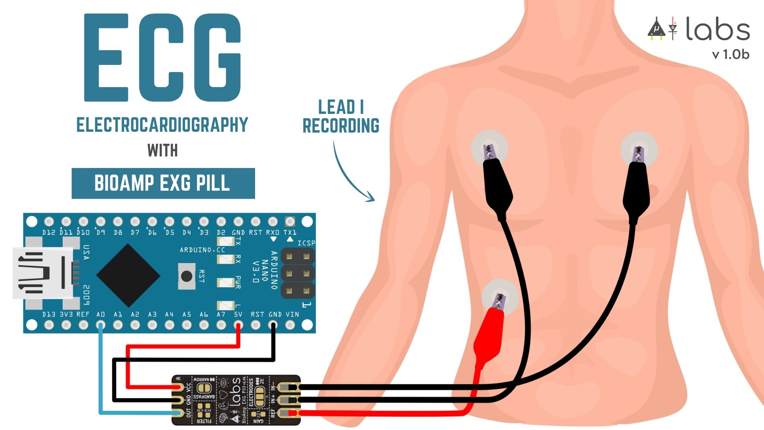
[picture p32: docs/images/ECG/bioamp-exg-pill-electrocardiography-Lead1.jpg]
Wiring and Electrode placement for chest ECG


<br>

<p style="text-align: center;"> <b> Chest ECG HeartBeat Detection Video </b></p>

<div class="video-container">

[Chest ECG HeartBeat Detection Video](https://www.youtube.com/embed/jNXJoB72sxU ':include :type=iframe frameborder=0')

</div>

<br>

- ### Hand EKG heartbeat detection

The BioAmp EXG pill is very sensitive to BioPotential signals, so you can even detect heart beats by connecting the electrodes to your hands (much like how an Apple watch records an ECG). To do this, first flash the <a href="https://github.com/upsidedownlabs/BioAmp-EXG-Pill/blob/main/software/HeartBeatDetection/HeartBeatDetection.ino" style="color: Red; text-decoration: none;"> Heart Beat Detection Arduino sketch </a> to your nano, and then hook up exactly the same wiring as above, and connect the electrodes like this:

1. IN- on LEFT wrist
2. IN+ on RIGHT wrist
3. REF on the back of any hand.

<br>

<p style="text-align: center;"> <b> Hand EKG HeartBeat Detection Arduino Sketch </b></p>

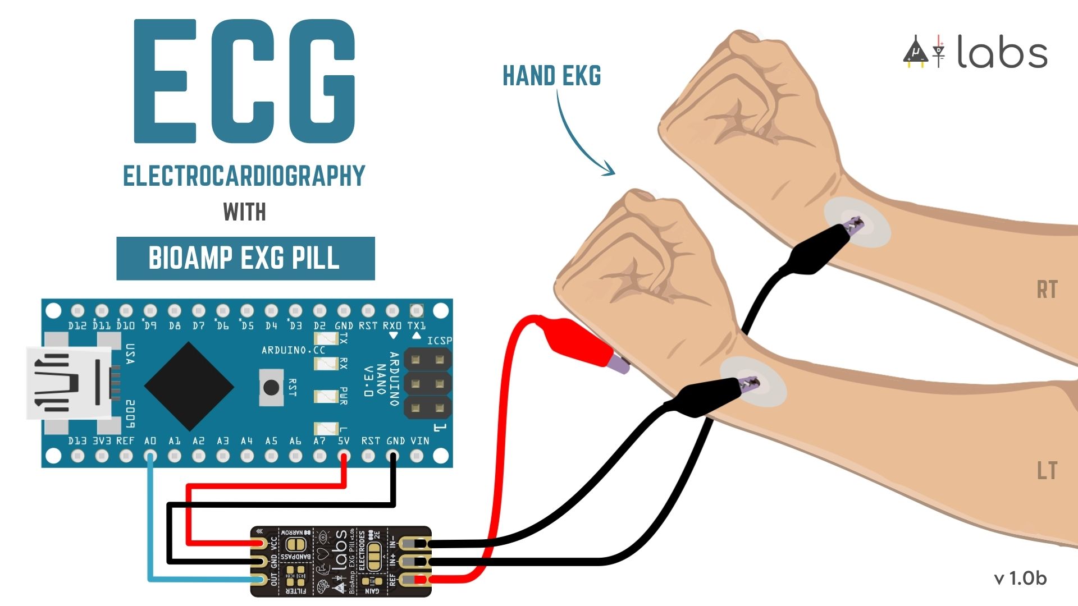
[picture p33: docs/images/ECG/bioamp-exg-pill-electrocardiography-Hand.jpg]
ecg-hand-diagram


<br><br>

<p style="text-align: center;"> <b> Hand EKG HeartBeat Detection Video </b></p>

<div class="video-container">

[Hand EKG HeartBeat Detection Video](https://www.youtube.com/embed/5rHjvKB7c1o ':include :type=iframe frameborder=0')

</div>

## References

1. Join the <a href="https://discord.gg/6aNknuBkfN" style="color: Red; text-decoration: none;">Upside Down Labs Discord server</a>  for chatting.
2. Subscribe to <a href="https://en.wikipedia.org/wiki/Electrooculography" style="color: Red; text-decoration: none;"> Electrooculography (EOG)</a>  to get notified when we do live.

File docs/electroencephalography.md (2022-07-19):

## Electroencephalography (EEG) &#129504;

 <a href="https://en.wikipedia.org/wiki/Electroencephalography" style="color: #ff3385; text-decoration: none;"> Electroencephalography (EEG) </a>  is an electrophysiological monitoring method to record the brain's electrical activity on the scalp. During the procedure, electrodes consisting of small metal discs with thin wires are pasted onto the scalp. The electrodes detect <a href="https://www.hopkinsmedicine.org/health/treatment-tests-and-therapies/electroencephalogram-eeg" style="color: #ff3385; text-decoration: none;">tiny electrical charges</a>  that result from brain-cell activity. Those charges are then amplified to appear on a computer screen. It is typically non-invasive, with the electrodes placed along the scalp. The resulting signal is called an electroencephalogram, an example of which is shown below:

<br>

<p style="text-align: center;"> <b> Resulting EEG Signal Wave </b></p>

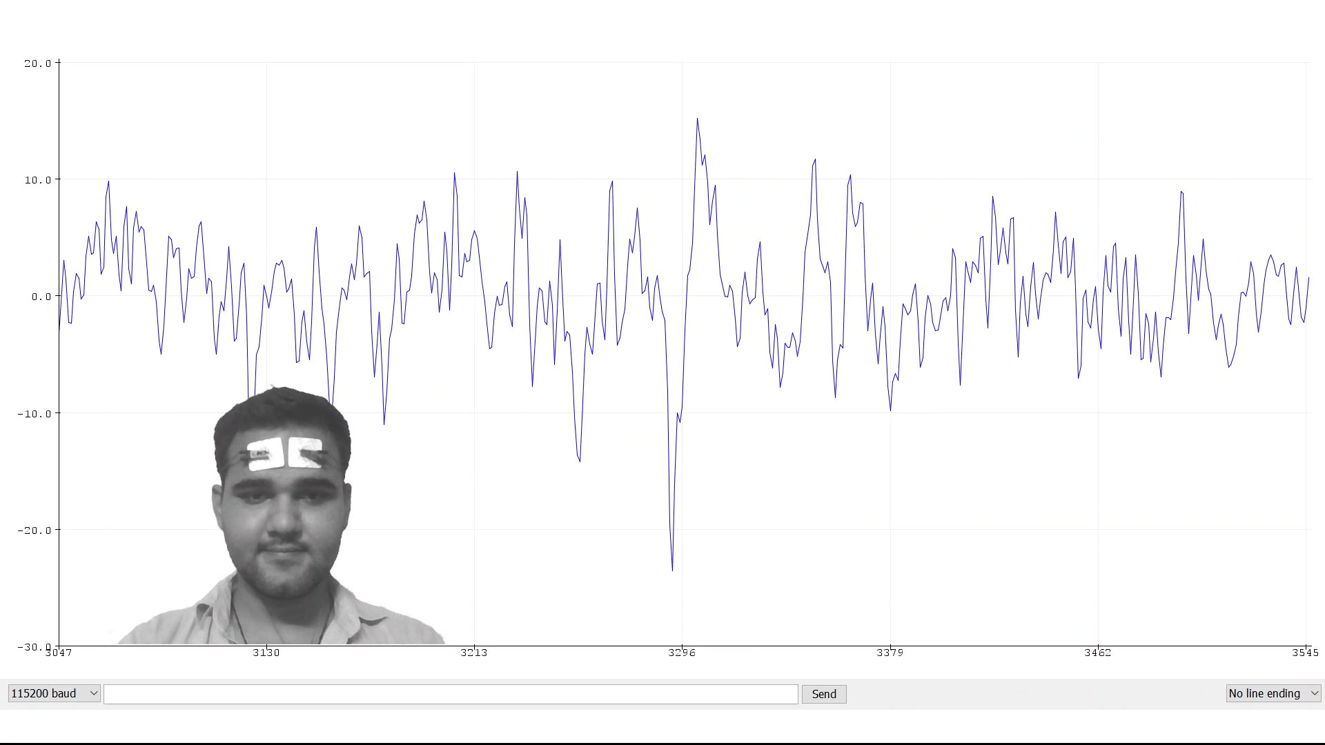
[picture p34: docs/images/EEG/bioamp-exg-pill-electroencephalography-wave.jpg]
Resulting EEG Signal Wave


## How to Create an Electroencephalograph With BioAmp EXG Pill?

An EEG is performed using an instrument called an electroencephalograph to produce a record called an electroencephalogram. Electrodes are commonly placed on the forehead, as shown in the diagram below, when recording frontal-cortex EEG signals.

<br>

<p style="text-align: center;"> <b> Frontal-Cortex EEG Signal Diagram </b></p>

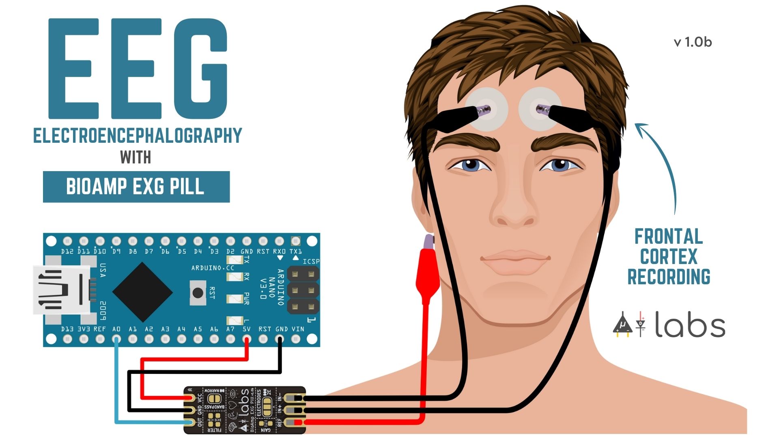
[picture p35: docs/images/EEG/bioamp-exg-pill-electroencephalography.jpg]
Frontal-Cortex EEG Signal Diagram


<br>

To record nice clean EEG signals with BioAmp EXG Pill, all you need is the Analog Serial Out sample Arduino sketch. If you want some more control we also have a <a href="https://github.com/upsidedownlabs/BioAmp-EXG-Pill/tree/main/software/FixedSampling/FixedSampling.ino" style="color:  #ff3385; text-decoration: none;"> Fixed Sampling example sketch</a> for recording EEG and other biopotential signals at a specific sampling rate. You can also use the <a href="https://github.com/upsidedownlabs/BioAmp-EXG-Pill/blob/main/software/EEGFilter/EEGFilter.ino" style="color:  #ff3385; text-decoration: none;"> EEG Filter example sketch </a>  for recording EEG at a sampling rate of 256.0 Hz and a frequency of 0.5 - 29.5 Hz. The image below shows the fourth-order Butterworth IIR digital bandpass filter used in the EEG Filter example sketch.

<br>

<p style="text-align: center;"> <b> EEG Filter sample Sketch </b></p>

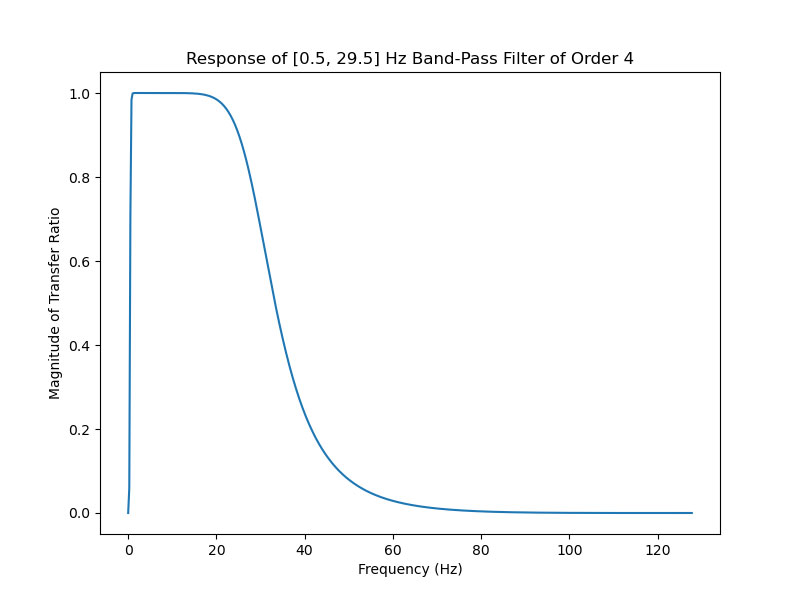
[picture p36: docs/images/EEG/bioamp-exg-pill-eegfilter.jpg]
EEG Filter Sketch


## Frontal EEG Recording

The video below shows a frontal electroencephalography (EEG) recording for both open- and closed-eye positions. The transition between the signals is also very clearly visible. To get an even better EEG signal, it's recommended to use a dedicated ADC like the Texas Instruments <a href="https://www.ti.com/product/ADS1115" style="color: #ff3385; text-decoration: none;"> ADS115 (16-bit) </a>  or <a href="https://www.ti.com/product/ADS131M08" style="color: #ff3385; text-decoration: none;"> ADS131M08 (24-bit) </a>. On the new BioAmp EXG Pill v1.0, we recommend creating a solder bridge on the back side of the PCB to set the narrow bandpass option.

<p style="text-align: center;"> <b> Frontal EEG Recording </b></p>

<div class="video-container">

[Frontal EEG Recording](https://player.vimeo.com/video/617188926?h=809ae189ee ':include :type=iframe frameborder=0')

</div>

<br>

_**Note**: BioAmp EXG Pill is not a certified medical device and should not be treated like one._

## References 

1. <a href="https://en.wikipedia.org/wiki/Electroencephalography" style="color: #ff3385; text-decoration: none;">https://en.wikipedia.org/wiki/Electroencephalography </a>
2. <a href="https://www.hopkinsmedicine.org/health/treatment-tests-and-therapies/electroencephalogram-eeg" style="color: #ff3385; text-decoration: none;"> https://www.hopkinsmedicine.org/health/treatment-tests-and-therapies/electroencephalogram-eeg </a>
3. <a href="https://github.com/upsidedownlabs/BioAmp-EXG-Pill" style="color: #ff3385; text-decoration: none;">https://github.com/upsidedownlabs/BioAmp-EXG-Pill</a>

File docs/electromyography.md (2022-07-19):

## Electromyography (EMG) &#128170;

<a href="https://en.wikipedia.org/wiki/Electromyography" style="color: #b38600; text-decoration: none;"> Electomyography (EMG) </a> is a technique for evaluating and recording the electrical activity produced by skeletal muscles. EMG is also used as a diagnostic procedure to assess the health of muscles and the nerve cells that control them (motor neurons). EMG results can reveal nerve dysfunction, muscle dysfunction, or problems with nerve-to-muscle signal transmission. The image below shows an EMG wave recorded with BioAmp EXG Pill.

<br>

<p style="text-align: center;"> <b> Resulting EMG Signal Wave </b></p>

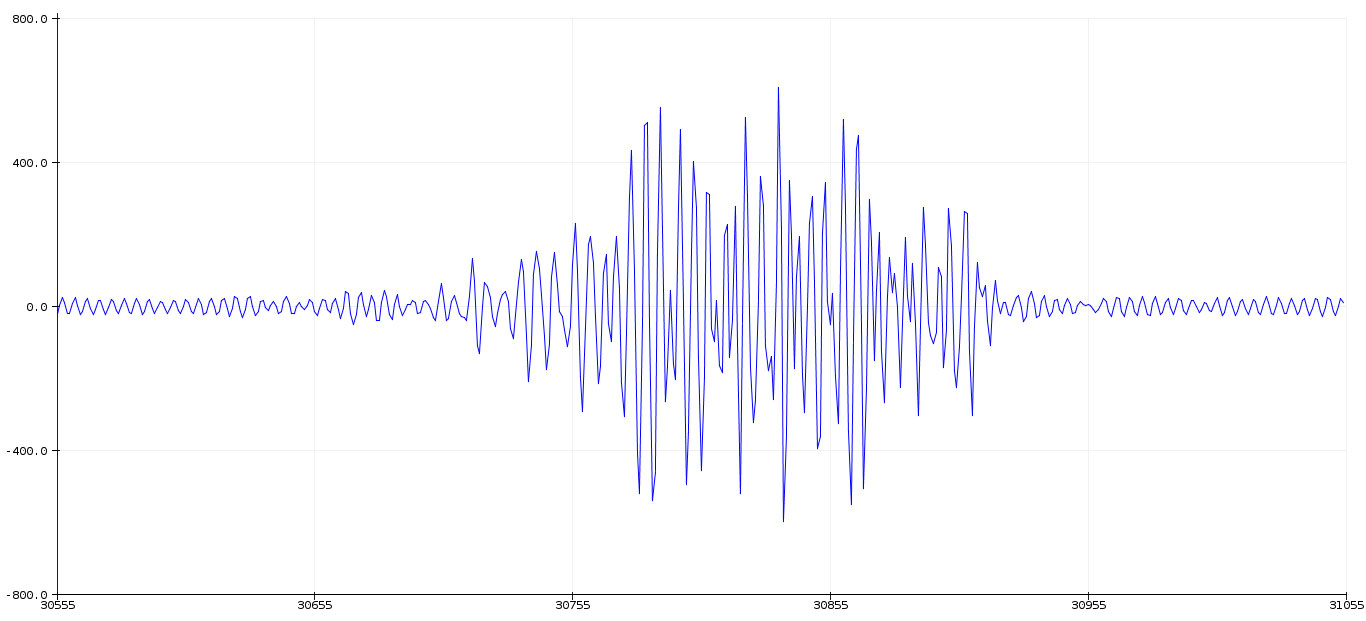
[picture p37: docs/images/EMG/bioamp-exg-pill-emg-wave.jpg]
emg-wave-diagram


<br>

## How to Create an Electromyograph with BioAmp EXG Pill?

EMG is performed using an instrument called an electromyograph to produce a record called an electromyogram. Common electrode placement for recording good EMG signal for hand movement is near the ulnar nerve, as shown in the diagram below.

<br>

<p style="text-align: center;"> <b> Hand Movement EMG Signal Diagram </b></p>

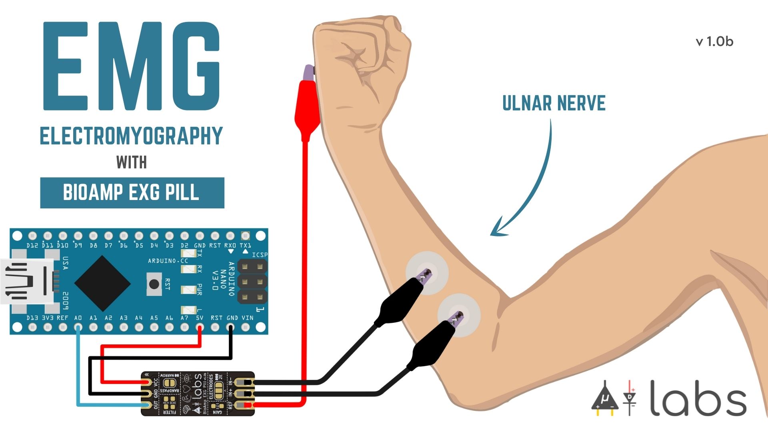
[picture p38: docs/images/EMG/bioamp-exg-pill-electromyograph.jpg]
hand-movement-emg-signal-diagram


<br>

To record nice clean EMG signals with BioAmp EXG Pill, all you need is the Analog Serial Out Arduino sketch. If you want more control we also have a <a href="https://github.com/upsidedownlabs/BioAmp-EXG-Pill/tree/main/software/FixedSampling/FixedSampling.ino" style="color: #b38600; text-decoration: none;"> Fixed Sampling Arduino sketch</a> that allows you to record EMG and other Biopotential signals at a specific sampling rate. You can also use the <a href="https://github.com/upsidedownlabs/BioAmp-EXG-Pill/blob/main/software/EMGFilter/EMGFilter.ino" style="color: #b38600; text-decoration: none;"> EMG Filter Arduino sketch</a> for recording EMG at a 500 Hz sampling rate and a 74.5 - 149.5 Hz frequency. The image below shows the 4th order bandpass Butterworth IIR digital filter used in the EMG Filter sample sketch:

<br>

<p style="text-align: center;"> <b> EMG Filter Sample Sketch </b></p>

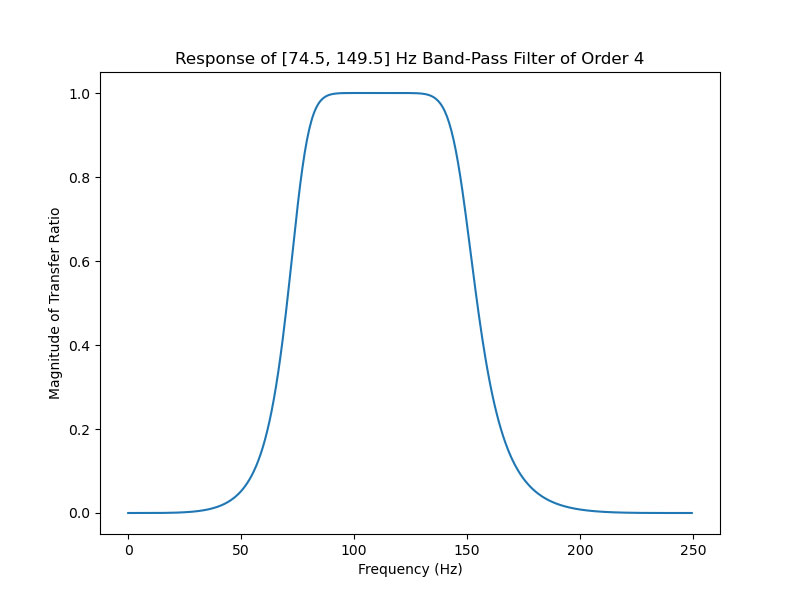
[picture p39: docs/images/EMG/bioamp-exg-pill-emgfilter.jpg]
emg-filter-sample-sketch


<br>

For practical use cases, we need a smooth signal, but the raw EMG signal does not come out as a smooth curve, which is why we offer the <a href="https://github.com/upsidedownlabs/BioAmp-EXG-Pill/tree/main/software/EMGEnvelop/EMGEnvelop.ino" style="color: #b38600; text-decoration: none;"> envelope-detection Arduino sketch</a> for BioAmp EXG Pill. The video below shows envelope detection at work:

<p style="text-align: center;"> <b> Envelope Detection Recording </b></p>

<div class="video-container">

[Envelope Detection Recording](https://player.vimeo.com/video/593798539?h=ef34fc28c3 ':include :type=iframe frameborder=0')

</div>

## Example EMG Projects with BioAmp EXG Pill

BioAmp EXG Pill allows you to do a lot with muscle power. We show two examples below: a servo controller and an LED bar graph. Both demonstrations use code that is derived from the <a href="https://github.com/upsidedownlabs/BioAmp-EXG-Pill/tree/main/software/EMGEnvelop/EMGEnvelop.ino" style="color: #b38600; text-decoration: none;"> envelope-detection Arduino sketch</a>. The image below shows how envelope detection works on the Raw EMG signal.

<br>

<p style="text-align: center;"> <b> EMG Envelope Wave </b></p>

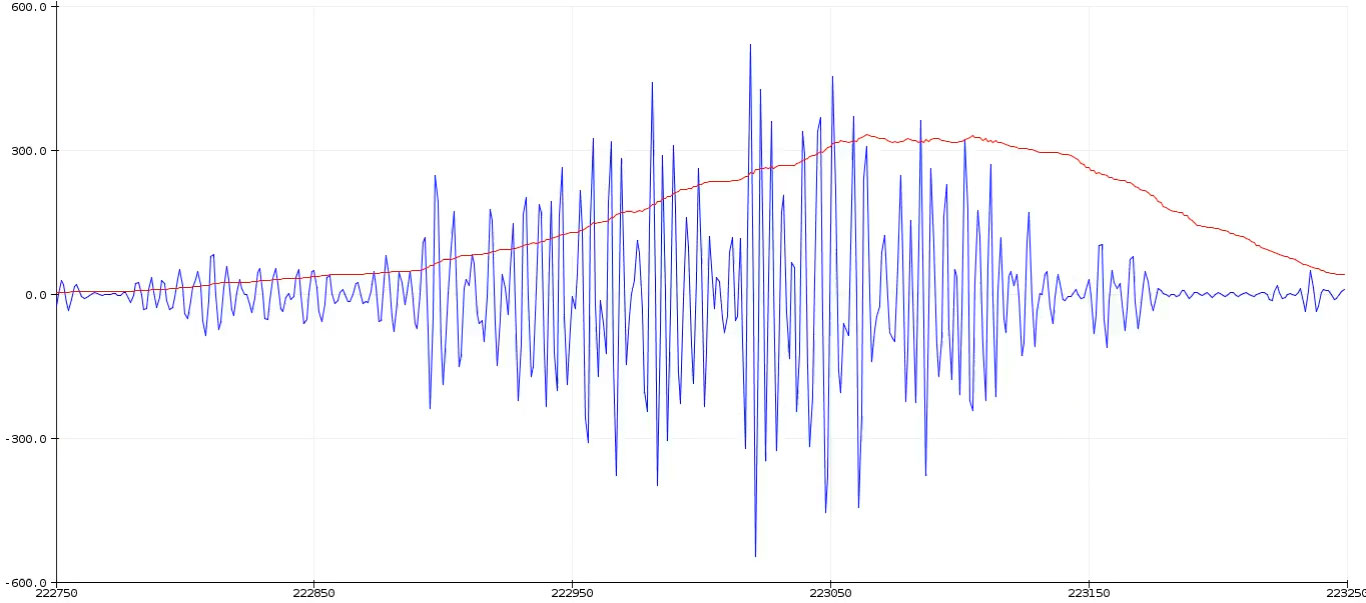
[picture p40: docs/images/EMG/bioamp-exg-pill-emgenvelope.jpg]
emg-envelope-wave


<br>

- ### Servo Controller

Controlling a servo motor with BioAmp EXG Pill is pretty easy, as shown in the video below. To create the same project, all you have to do is load the <a href="https://github.com/upsidedownlabs/BioAmp-EXG-Pill/tree/main/software/ServoControl/ServoControl.ino" style="color: #b38600; text-decoration: none;"> servo-control Arduino sketch</a> onto your Arduino-compatible board, and you're good to go.

<br>

<p style="text-align: center;"> <b> Servo-Control using BioAmp EXG pill </b></p>

<div class="video-container">

[Servo-Control using BioAmp EXG pill](https://www.youtube.com/embed/ZePE1umyzFI ':include :type=iframe frameborder=0')

</div>

<br><br>

- ### LED Bar Graph

The same envelope-detection concept is used for the LED bar graph project. You can use as many LEDs you want with this project. To make a cool LED bar graph like the one shown in the video below, just edit the <a href="https://github.com/upsidedownlabs/BioAmp-EXG-Pill/tree/main/software/LEDBarGraph/LEDBarGraph.ino" style="color: #b38600; text-decoration: none;"> LED bar graph Arduino sketch </a> , upload it to the Arduino board, then connect the LEDs according to the specified pin numbers.

<br>

<p style="text-align: center;"> <b> LED Bar Graph Project using BioAmp EXG Pill </b></p>

<div class="video-container">

[LED Bar Graph Project using BioAmp EXG Pill](https://www.youtube.com/embed/MzLAFVXk7_M ':include :type=iframe frameborder=0')

</div>

## References

1. <a href="https://www.mayoclinic.org/tests-procedures/emg/about/pac-20393913" style="color: #b38600; text-decoration: none;"> Mayo Clinic article on EMG</a>
2. <a href="https://en.wikipedia.org/wiki/Electromyography" style="color: #b38600; text-decoration: none;"> Wikipedia Electromyography page</a>
3. <a href="https://www.instructables.com/Claw-Controller-Using-BIOAMP-EXG-PILL/" style="color: #b38600; text-decoration: none;"> PR ROBOTICS _Instructables_ article on _Claw Controller Using BioAmp EXG PILL_</a>
4. <a href="https://github.com/upsidedownlabs/BioAmp-EXG-Pill" style="color: #b38600; text-decoration: none;"> Upside Down Labs - BioAmp EXG Pill Github repository</a>

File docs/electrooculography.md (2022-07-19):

## Electrooculography (EOG) &#128065;

<a href="https://en.wikipedia.org/wiki/Electrooculography" style="color: brown; text-decoration: none;"> Electrooculography (EOG)</a>
  is a technique for measuring the corneo-retinal standing potential that exists between the front and the back of the human eye. The resulting signal is called the electrooculogram.

  <br>

<p style="text-align: center;"> <b> Resulting EOG Signal Wave </b></p>

eog-demo-diagram

<br><br>

To measure eye movement, pairs of electrodes are typically placed either above and below the eye or to the left and right of the eye. If the eye moves from center position toward one of the two electrodes, this electrode "sees" the positive side of the retina and the opposite electrode "sees" the negative side of the retina. Consequently, a potential difference occurs between the electrodes. Assuming the resting potential is constant, the recorded potential is a measure of the eye's position.

## How to Create an Electrooculograph With BioAmp EXG Pill

EOG is performed using an instrument called an electrooculograph to produce a record called an electrooculogram. Common electrode placement for recording good EOG signal for eye movement (vertical and horizontal) is shown in the diagram below.

<br>

<p style="text-align: center;"> <b> EOG Electrode Placement Diagram </b></p>

eog-electrode-placement

To record nice clean EOG signals with BioAmp EXG Pill, all you need is the Analog Serial Out Arduino example sketch. If you want some more control we also have a <a href="https://github.com/upsidedownlabs/BioAmp-EXG-Pill/tree/main/software/FixedSampling" style="color: brown; text-decoration: none;"> Fixed Sampling example sketch</a>
 for recording EOG and other biopotential signals at a specific sampling rate. You can also use the <a href="https://github.com/upsidedownlabs/BioAmp-EXG-Pill/blob/main/software/EOGFilter/EOGFilter.ino" style="color: brown; text-decoration: none;"> EOG Filter example sketch</a>  for recording EOG at a sampling rate of 75.0 Hz and a frequency of 0.5 - 19.5 Hz. The image below shows the fourth-order Butterworth IIR digital bandpass filter used in the EOG Filter example sketch.

<br>

<p style="text-align: center;"> <b> EOG-Filter sample sketch </b></p>

eog-filter

_**Note**: BioAmp EXG Pill is not a certified medical device and should not be treated like one._

## Recording Horizontal Eye Movement

To record horizontal eye movement, place the electrodes near your left and right eyes, just like in the image shown below. Then you just have to flash the <a href="https://github.com/upsidedownlabs/BioAmp-EXG-Pill/blob/main/software/EOGFilter/EOGFilter.ino" style="color: brown; text-decoration: none;"> EOG filter program </a>  onto your MCU, complete the wiring, and connect the electrodes like this:

1. `IN-` near right eye
2. `IN+` near left eye
3. `REF` behind ear

<br>

<p style="text-align: center;"> <b> Horizontal Eye-Movement Diagram </b></p>

horizontal-eye-movement-diagram

<br>

<p style="text-align: center;"> <b> Horizontal Eye-Movement Recording</b></p>

<div class="video-container">

[Horizontal Eye-Movement Recording](https://player.vimeo.com/video/605740636?h=68382bb00a ':include :type=iframe frameborder=0')

</div>

<br>

## Recording Vertical Eye Movement

To record vertical eye movement, place the electrodes above and below your left or right eye, just like in the image shown below. Then, just like before, flash the <a href="https://github.com/upsidedownlabs/BioAmp-EXG-Pill/blob/main/software/EOGFilter/EOGFilter.ino" style="color: brown; text-decoration: none;"> EOG filter program </a> onto your MCU, complete the wiring, and connect the electrodes like this:

1. `IN-` above eye
2. `IN+` below eye
3. `REF` behind ear

<br>

<p style="text-align: center;"> <b> Vertical Eye-Movement Diagram </b></p>

vertical-eye-movement-diagram

## Eye-Blink Detection

Eye blinks can also be recorded with the same electrode placement. Although we used an Arduino Nano for our testing, you can flash the <a href="https://github.com/upsidedownlabs/BioAmp-EXG-Pill/blob/main/software/EyeBlinkDetection/EyeBlinkDetection.ino" style="color: brown; text-decoration: none;"> Arduino eye-blink detection sketch</a>
onto any Arduino-compatible board and use it to detect eye blinks. The video below shows a working demo:

<br>

<p style="text-align: center;"> <b> Eye Blink Detection Recording </b></p>

<div class="video-container">

[Eye Blink Detection Recording](https://player.vimeo.com/video/605736032?h=bf6b7bcb55 ':include :type=iframe frameborder=0')

</div>

## References

1. <a href="https://en.wikipedia.org/wiki/Electrooculography" style="color: brown; text-decoration: none;"> https://en.wikipedia.org/wiki/Electrooculography</a>
2. <a href="https://github.com/ChinmayLonkar/MarioEMG" style="color: brown; text-decoration: none;">https://github.com/ChinmayLonkar/MarioEMG</a>
3. <a href="https://github.com/upsidedownlabs/BioAmp-EXG-Pill" style="color: brown; text-decoration: none;">https://github.com/upsidedownlabs/BioAmp-EXG-Pill</a>

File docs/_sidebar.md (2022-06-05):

- [__Home__](/)
- Getting started

  - [Overview](overview.md)
  - [Projects](projects.md)
  - [Connections](connections.md)

- Applications

  - [Electrooculography](electrooculography.md)
  - [Electromyography](electromyography.md)
  - [Electroencephalography](electroencephalography.md)
  - [Electrocardiography](electrocardiography.md)

- Software

  - [EOG Software](eog_software.md)
  - [EMG Software](emg_software.md)
  - [EEG Software](eeg_software.md)
  - [ECG Software](ecg_software.md)

- Hardware
  - [Arduino](arduino.md)
  - [ESP32](esp32.md)
  - [RPi Pico](pico.md)
  - [STM32](stm32.md)
  - [BBBW](bbbw.md)

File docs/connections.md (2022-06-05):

This page will describe all connections and wiring daigram of Bio-Amp-EXG-pill.

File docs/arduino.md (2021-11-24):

This section will contain info about using Bio-Amp-EXG-Pill with arduino.

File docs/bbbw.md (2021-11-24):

This section will contain info about using Bio-Amp-EXG-Pill with bbbw board.

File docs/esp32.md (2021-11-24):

This section will contain info about using Bio-Amp-EXG-Pill with ESP32.

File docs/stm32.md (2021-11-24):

This section will contain info about using Bio-Amp-EXG-Pill with STM32 Blue Pill.

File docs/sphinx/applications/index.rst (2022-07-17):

Applications
============

1. :ref:`Electrocardiography <open0>`
2. :ref:`Electroencephalography <open1>`
3. :ref:`Electromyography <open2>`
4. :ref:`Electrooculography <open3>`

.. _open0:

Electrocardiography 
**********************
		
We are delighted to share that BioAmp EXG Pill is among the top ten `Winners Of The Hackaday Prize Supportive Tech Challenge <https://hackaday.com/2021/08/31/ten-winners-of-the-hackaday-prize-supportive-tech-challenge/>`_ .It was all possible because of various `Arduino example sketches <https://github.com/upsidedownlabs/BioAmp-EXG-Pill/tree/main/software>`_ and projects that are available for the BioAmp EXG Pill which you can use to create a supportive technology. For example, you can create a mobile heart ailment detection machine, prosthetic hand controller, EOG-based game controller, and many more similar projects. Let's take a look at how you can use BioAmp EXG Pill to detect heartbeats and potentially create a real-time heart monitor.

**Detecting heartbeats with BioAmp EXG Pill & Arduino Nano**
------------------------------------------------------------

Bioamp-EXG-Pill Electrocardiography-wave diagram

   Bioamp-EXG-Pill Electrocardiography-wave

To record ECG and detect a heartbeat in that ECG on an Arduino Nano you first need to flash the `Heart Beat Detection Arduino sketch <https://github.com/upsidedownlabs/BioAmp-EXG-Pill/blob/main/software/HeartBeatDetection/HeartBeatDetection.ino>`_  onto your Nano and then connect the electrodes either on your chest or hands.    

.. note ::

   BioAmp EXG Pill is not a certified medical device and shouldn't be treated like one.

|

**1. Chest ECG heartbeat detection**
------------------------------------

A very basic method for detecting heartbeats is to place the electrodes near the heart, as shown below. You just Heart have to flash the `Heart beat Detection Arduino sketch <https://github.com/upsidedownlabs/BioAmp-EXG-Pill/blob/main/software/HeartBeatDetection/HeartBeatDetection.ino>`_ to your Nano, do the wiring, and connect the electrodes like this:

1. IN- near LEFT shoulder
2. IN+ near RIGHT shoulder
3. REF above Right leg

|

Wiring and Electrode placement for chest ECG

   Wiring and Electrode placement for chest ECG

|

.. raw:: html
    
   <iframe width="540" height="320" style="display:block; margin:0 auto;" src="https://www.youtube.com/embed/jNXJoB72sxU" title="YouTube video player" frameborder="0" allow="accelerometer; autoplay; clipboard-write; encrypted-media; gyroscope; picture-in-picture" allowfullscreen ></iframe>

|

**2. Hand EKG heartbeat detection**
-----------------------------------

The BioAmp EXG pill is very sensitive to BioPotential signals, so you can even detect heart beats by connecting the electrodes to your hands (much like how an Apple watch records an ECG). To do this, first flash the `Heart Beat Detection Arduino sketch <https://github.com/upsidedownlabs/BioAmp-EXG-Pill/blob/main/software/HeartBeatDetection/HeartBeatDetection.ino>`_ to your nano, and then hook up exactly the same wiring as above, and connect the electrodes like this:

1. IN- on LEFT wrist
2. IN+ on RIGHT wrist
3. REF on the back of any hand.

|

Bioamp-EXG-Pill Electrocardiography-hand

   Bioamp-EXG-Pill Electrocardiography-hand

|

**References**
--------------

1. Join the `Upside Down Labs Discord server <https://discord.gg/6aNknuBkfN>`_ for chatting.
2. Subscribe to `Electrooculography (EOG) <https://en.wikipedia.org/wiki/Electrooculography>`_ to get notified when we do live.

|

.. _open1:

Electroencephalography 
**************************

`Electroencephalography (EEG) <https://en.wikipedia.org/wiki/Electroencephalography>`_ is an electrophysiological monitoring method to record the brain's electrical activity on the scalp. During the procedure, electrodes consisting of small metal discs with thin wires are pasted onto the scalp. The electrodes detect `tiny electrical charges <https://www.hopkinsmedicine.org/health/treatment-tests-and-therapies/electroencephalogram-eeg>`_ that result from brain-cell activity. Those charges are then amplified to appear on a computer screen. It is typically non-invasive, with the electrodes placed along the scalp. The resulting signal is called an electroencephalogram, an example of which is shown below:

 Bioamp-EXG-Pill Electroencephalography-wave

    Bioamp-EXG-Pill Electroencephalography-wave

|

**Creating Electroencephalograph With BioAmp EXG Pill**
-------------------------------------------------------

An EEG is performed using an instrument called an electroencephalograph to produce a record called an electroencephalogram. Electrodes are commonly placed on the forehead, as shown in the diagram below, when recording frontal-cortex EEG signals.

  Bioamp-EXG-Pill Electroencephalography

     Bioamp-EXG-Pill Electroencephalography

|

To record nice clean EEG signals with BioAmp EXG Pill, all you need is the Analog Serial Out sample Arduino sketch. If you want some more control we also have a `Fixed Sampling example sketch <https://github.com/upsidedownlabs/BioAmp-EXG-Pill/tree/main/software/FixedSampling/FixedSampling.ino>`_ for recording EEG and other biopotential signals at a specific sampling rate. You can also use the `EEG Filter example sketch <https://github.com/upsidedownlabs/BioAmp-EXG-Pill/blob/main/software/EEGFilter/EEGFilter.ino>`_ for recording EEG at a sampling rate of 256.0 Hz and a frequency of 0.5 - 29.5 Hz. The image below shows the fourth-order Butterworth IIR digital bandpass filter used in the EEG Filter example sketch.

  bioamp-exg-pill EEG filter

     Bioamp-EXG-Pill EEG filter

|

**Frontal EEG Recording**
-------------------------

The video below shows a frontal electroencephalography (EEG) recording for both open- and closed-eye positions. The transition between the signals is also very clearly visible. To get an even better EEG signal, it's recommended to use a dedicated ADC like the Texas Instruments `ADS115 (16-bit) <https://www.ti.com/product/ADS1115>`_ or `ADS131M08 (24-bit) <https://www.ti.com/product/ADS131M08>`_  .On the new BioAmp EXG Pill v1.0, we recommend creating a solder bridge on the back side of the PCB to set the narrow bandpass option.

.. raw:: html                                                                              
                                                                                             
   <iframe title="vimeo-player" src="https://player.vimeo.com/video/617188926?h=809ae189ee" width="540" height="320" style="display:block; margin:0 auto;" frameborder="0" allowfullscreen></iframe>                        

.. note:: 

   BioAmp EXG Pill is not a certified medical device and should not be treated like one.

**References**
--------------

1. `https://en.wikipedia.org/wiki/Electroencephalography <https://en.wikipedia.org/wiki/Electroencephalography>`_
2. `https://www.hopkinsmedicine.org/health/tests-and-therapies/electroencephalogram-eeg <https://www.hopkinsmedicine.org/health/treatment-tests-and-therapies/electroencephalogram-eeg>`_
3. `https://github.com/upsidedownlabs/BioAmp-EXG-Pill <https://github.com/upsidedownlabs/BioAmp-EXG-Pill>`_

| 

.. _open2:

Electromyography 
*********************

`Electomyography (EMG) <https://en.wikipedia.org/wiki/Electromyography>`_ is a technique for evaluating and recording the electrical activity produced by skeletal muscles. EMG is also used as a diagnostic procedure to assess the health of muscles and the nerve cells that control them (motor neurons). EMG results can reveal nerve dysfunction, muscle dysfunction, or problems with nerve-to-muscle signal transmission. The image below shows an EMG wave recorded with BioAmp EXG Pill.

  Bioamp-EXG-Pill EMG Wave

     BioAmp-EXG-Pill EMG Wave                                              

|

**How to Create an Electromyograph with BioAmp EXG Pill?**
----------------------------------------------------------

EMG is performed using an instrument called an electromyograph to produce a record called an electromyogram. Common electrode placement for recording good EMG signal for hand movement is near the ulnar nerve, as shown in the diagram below.

  BioAmp-EXG-Pill-Electromyograph

     Bioamp-EXG-Pill-Electromyograph                                                     

|

To record nice clean EMG signals with BioAmp EXG Pill, all you need is the Analog Serial Out Arduino sketch. If you want more control we also have a `Fixed Sampling Arduino sketch <https://github.com/upsidedownlabs/BioAmp-EXG-Pill/tree/main/software/FixedSampling/FixedSampling.ino>`_ that allows you to record EMG and other Biopotential signals at a specific sampling rate. You can also use the `EMG Filter Arduino sketch <https://github.com/upsidedownlabs/BioAmp-EXG-Pill/blob/main/software/EMGFilter/EMGFilter.ino>`_ for recording EMG at a 500 Hz sampling rate and a 74.5 - 149.5 Hz frequency. The image below shows the 4th order bandpass Butterworth IIR digital filter used in the EMG Filter sample sketch:

 BioAmp-EXG-Pill-EMG Filter

    Bioamp-EXG-Pill EMG Filter                                              

|

For practical use cases, we need a smooth signal, but the raw EMG signal does not come out as a smooth curve, which is why we offer the `envelope-detection Arduino sketch <https://github.com/upsidedownlabs/BioAmp-EXG-Pill/tree/main/software/EMGEnvelop/EMGEnvelop.ino>`_ for BioAmp EXG Pill. The video below shows envelope detection at work:

.. raw:: html                                                                               
                                                                                             
   <iframe title="vimeo-player" src="https://player.vimeo.com/video/593798539?h=ef34fc28c3" width="540" height="320" style="display:block; margin:0 auto;" frameborder="0" allowfullscreen></iframe>                        

 |

**Example EMG Projects with BioAmp EXG Pill**
---------------------------------------------

BioAmp EXG Pill allows you to do a lot with muscle power. We show two examples below: a servo controller and an LED bar graph. Both demonstrations use code that is derived from the `envelope-detection Arduino sketch <https://github.com/upsidedownlabs/BioAmp-EXG-Pill/tree/main/software/EMGEnvelop/EMGEnvelop.ino>`_ . The image below shows how envelope detection works on the Raw EMG signal.

 Bioamp-EXG-Pill EMG Envelope

    Bioamp-EXG-Pill EMG Envelope                                                 

|

* Servo Controller

Controlling a servo motor with BioAmp EXG Pill is pretty easy, as shown in the video below. To create the same project, all you have to do is load the `servo-control Arduino sketch <https://github.com/upsidedownlabs/BioAmp-EXG-Pill/tree/main/software/ServoControl/ServoControl.ino>`_ onto your Arduino-compatible board, and you're good to go.

.. raw:: html                                                                                    
                                                                                                  
   <iframe width="540" height="320" style="display:block; margin:0 auto;" src="https://www.youtube.com/embed/ZePE1umyzFI" title="YouTube video player" frameborder="0" allow="accelerometer; autoplay; clipboard-write; encrypted-media; gyroscope; picture-in-picture" allowfullscreen></iframe>                     

|

* LED Bar Graph

The same envelope-detection concept is used for the LED bar graph project. You can use as many LEDs you want with this project. To make a cool LED bar graph like the one shown in the video below, just edit the `LED bar graph Arduino sketch <https://github.com/upsidedownlabs/BioAmp-EXG-Pill/tree/main/software/LEDBarGraph/LEDBarGraph.ino>`_ , upload it to the Arduino board, then connect the LEDs according to the specified pin numbers.

.. raw:: html                                                                                    
                                                                                                  
   <iframe width="540" height="320" style="display:block; margin:0 auto;" src="https://www.youtube.com/embed/MzLAFVXk7_M" title="YouTube video player" frameborder="0" allow="accelerometer; autoplay; clipboard-write; encrypted-media; gyroscope; picture-in-picture" allowfullscreen></iframe>                     

|

**References**
--------------

1. `Mayo Clinic article on EMG <https://www.mayoclinic.org/tests-procedures/emg/about/pac-20393913>`_ 
2. `Wikipedia Electromyography page <https://en.wikipedia.org/wiki/Electromyography>`_ 
3. `PR ROBOTICS Instructables article on Claw Controller Using BioAmp EXG PILL <https://www.instructables.com/Claw-Controller-Using-BIOAMP-EXG-PILL/>`_ 
4. `Upside Down Labs - BioAmp EXG Pill Github repository <https://github.com/upsidedownlabs/BioAmp-EXG-Pill>`_ 

|

.. _open3:

Electrooculography 
**********************

`Electrooculography (EOG) <https://en.wikipedia.org/wiki/Electrooculography>`_ is a technique for measuring the corneo-retinal standing potential that exists between the front and the back of the human eye. The resulting signal is called the electrooculogram.

Bioamp-EXG-Pill EOG-Demo

   Bioamp-EXG-Pill EOG-Demo                                                 

|

To measure eye movement, pairs of electrodes are typically placed either above and below the eye or to the left and right of the eye. If the eye moves from center position toward one of the two electrodes, this electrode "sees" the positive side of the retina and the opposite electrode "sees" the negative side of the retina. Consequently, a potential difference occurs between the electrodes. Assuming the resting potential is constant, the recorded potential is a measure of the eye's position.

|

**How to Create an Electrooculograph With BioAmp EXG Pill?**
------------------------------------------------------------

EOG is performed using an instrument called an electrooculograph to produce a record called an electrooculogram. Common electrode placement for recording good EOG signal for eye movement (vertical and horizontal) is shown in the diagram below.
                                                                                                      
Bioamp-EXG-Pill EOG Electrode Placement

   Bioamp-EXG-Pill EOG Electrode Placement                                                                

|

To record nice clean EOG signals with BioAmp EXG Pill, all you need is the Analog Serial Out Arduino example sketch. If you want some more control we also have a `Fixed Sampling example sketch <https://github.com/upsidedownlabs/BioAmp-EXG-Pill/tree/main/software/FixedSampling>`_ for recording EOG and other biopotential signals at a specific sampling rate. You can also use the `EOG Filter example sketch <https://github.com/upsidedownlabs/BioAmp-EXG-Pill/blob/main/software/EOGFilter/EOGFilter.ino>`_ for recording EOG at a sampling rate of 75.0 Hz and a frequency of 0.5 - 19.5 Hz. The image below shows the fourth-order Butterworth IIR digital bandpass filter used in the EOG Filter example sketch.

Bioamp-EXG-Pill EOG Filter

   Bioamp-EXG-Pill EOG Filter                                                   

.. note:: 
    
   BioAmp EXG Pill is not a certified medical device and should not be treated like one.

|

**Recording Horizontal Eye Movement**
-------------------------------------

To record horizontal eye movement, place the electrodes near your left and right eyes, just like in the image shown below. Then you just have to flash the `EOG filter program <https://github.com/upsidedownlabs/BioAmp-EXG-Pill/blob/main/software/EOGFilter/EOGFilter.ino>`_ onto your MCU, complete the wiring, and connect the electrodes like this:

1. `IN-` near right eye
2. `IN+` near left eye
3. `REF` behind ear

|                                                                                                                        

 BioAmp EXG Pill Horizontal Eye-Movement

    BioAmp EXG Pill Horizontal Eye-Movement        

.. raw:: html

   <iframe title="vimeo-player" src="https://player.vimeo.com/video/605740636?h=68382bb00a" width="540" height="320" style="display:block; margin:0 auto;" frameborder="0" allowfullscreen></iframe>

**Recording Vertical Eye Movement**
-----------------------------------

To record vertical eye movement, place the electrodes above and below your left or right eye, just like in the image shown below. Then, just like before, flash the `EOG filter program  <https://github.com/upsidedownlabs/BioAmp-EXG-Pill/blob/main/software/EOGFilter/EOGFilter.ino>`_ onto your MCU, complete the wiring, and connect the electrodes like this:

1. `IN-` above eye
2. `IN+` below eye
3. `REF` behind ear

BioAmp EXG Pill Electrooculography-vertical

   BioAmp EXG Pill Electrooculography-vertical                                                                    

**Eye-Blink Detection**
-----------------------

Eye blinks can also be recorded with the same electrode placement. Although we used an Arduino Nano for our testing, you can flash the `Arduino eye-blink detection sketch <https://github.com/upsidedownlabs/BioAmp-EXG-Pill/blob/main/software/EyeBlinkDetection/EyeBlinkDetection.ino>`_
onto any Arduino-compatible board and use it to detect eye blinks. The video below shows a working demo:

.. raw:: html                                                                               
                                                                                             
   <iframe title="vimeo-player" src="https://player.vimeo.com/video/605736032?h=bf6b7bcb55" width="540" height="320" style="display:block; margin:0 auto;" frameborder="0" allowfullscreen></iframe>                        

|

**References**
--------------

1. `https://en.wikipedia.org/wiki/Electrooculography <https://en.wikipedia.org/wiki/Electrooculography>`_
2. `https://github.com/ChinmayLonkar/MarioEMG <https://github.com/ChinmayLonkar/MarioEMG>`_
3. `https://github.com/upsidedownlabs/BioAmp-EXG-Pill <https://github.com/upsidedownlabs/BioAmp-EXG-Pill>`_

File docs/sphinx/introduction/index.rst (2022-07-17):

Introduction
============

BioAmp EXG Pill is a small (2.54 X 1.00 cm) and elegant Analog Front End (AFE) board for BioPotential signal acquisition that you can use with any 5v Micro Controller Unit (MCU) with an ADC. It is capable of recording publication grade BioPotential signals like ECG, EMG, EOG, and EEG without the inclusion of any dedicated Hardware/Software filter, see `BioAmp EXG Pill v0.7 intro video <https://www.youtube.com/watch?v=-G3z9fvQnuw>`_ for more info. The v1.0 of BioAmp EXG pill provides even more flexibilty with configuration option for Gain, BandPass, Filter, and Electrodes.

BioAmp-EXG-Pill-Assembled

   BioAmp-EXG-Pill-Assembled

|                                                                   

Connection

   BioAmp-EXG-Pill-Connections                                                                                                                 

Configuration

   BioAmp-EXG-Pill-Configuration

|

BioAmp-EXG-Pill Basic-circuit
   
   BioAmp-EXG-Pill Basic-circuit



   BioAmp-EXG-Pill Electomyograph



   BioAmp-EXG-Pill Electrooculography-horizontal



   BioAmp-EXG-Pill Electrooculography-vertical

Electrocardiography (ECG) Lead-1

   BioAmp-EXG-Pill Electrocardiography (ECG) Lead-1

Electroencephalography (EEG)

   BioAmp-EXG-Pill Electroencephalography (EEG)

Software
********

BioAmp EXG Pill works with any 5V microcontroller with an ADC like Arduino UNO/Nano or you can use dedicated 5v compatible ADC like ADS1115. To help with signal processing and cleaning you can use the included Arduino example sketches listed below.

.. list-table::
   :class: longtable
   :widths: 7 25 60
   :header-rows: 1
   
   * - SNO.
     - Program
     - Description
   * - 1.
     - `FixedSampling <#>`_
     - Sample from ADC at a fixed rate for easy processing of signal.
   * - 2.
     - `EMGFilter <#>`_
     - A 74.5 - 149.5 Hz band pass filter sketch for clean Electromyography.
   * - 3. 
     - `ECGFilter <#>`_
     -  A 0.5 - 44.5 Hz band-pass filter sketch for clean Electrocardiography.
   * -  4. 
     - `EOGFilter <#>`_
     - A 0.5 - 19.5 Hz band-pass filter sketch for clean Electrooculography.
   * - 5. 
     - `EEGFilter <#>`_
     - A 0.5 - 29.5 Hz band-pass filter sketch for clean Electroencephalography.
   * - 6. 
     - `EMGEnvelop <#>`_
     - EMG signal envelop detection for robotics and biomedical applications.
   * - 7. 
     - `LEDBarGraph <#>`_
     - LED bar graph showing EMG amplitude.
   * - 8. 
     - `ServoControl <#>`_
     - Servo motor control with EMG.
   * - 9. 
     - `HeartBeatDetection <#>`_
     - Standard deviation based heart beat detection algorithm.
   * - 10. 
     - `EyeBlinkDetection <#>`_
     - EOG based eye blink detection.
   * - 11. 
     - `DrowsinessDetection <#>`_
     - Drowsiness detection using eye blink detection.
   * - 12. 
     - `ClawController <#>`_
     - Servo claw controller 
   * - 13. 
     - `EOGPhotoCaptureBLE <#>`_
     - EOG based photo clicking machine using ESP32 BLE 

**To-Do:**

.. list-table::
   :class: longtable 
   :widths: 7 25 60
   :header-rows: 1

   * - No. 
     - Program
     - Description 
   * - 1. 
     - BrainWaves 
     - Brain waves amplitude with FFT.
   * - 2. 
     - EOGController 
     - EOG based eye movement detection (left/right) to create a game controller.

Hardware
********

BioAmp EXG Pill has been created using KiCad and all the design files can be found under `hardware <#>`_ folder, including production `Gerber <#>`_ files. Images below shows a quick overview of the hardware design.

|

Bioamp-EXG-Pill Front

   Bioamp-EXG-Pill Front 

Bioamp-EXG-Pill Back

   Bioamp-EXG-Pill Back 

Bioamp EXG Pill v1-Beta-Black

   Bioamp EXG Pill v1-Beta-Black

BioAmp-EXG-Pill Dimensions & Schematic
---------------------------------------

+----------------------------------------------------------------------+---------------------------------------------------------------------------+
| 
|    :width: 150px                                                     |     :width: 450px                                                         |
|    :alt: Dimensions diagram                                          |     :alt: Schematic                                                       |                                                                 
|                                                                      |                                                                           |             
|    Bioamp-exg-pill Dimensions                                        |     Schematic                                                             |            
+----------------------------------------------------------------------+---------------------------------------------------------------------------+

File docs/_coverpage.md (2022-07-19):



# Bioamp-EXG-Pill <small>v1.0</small> 
<br>
<br>


[GitHub](https://github.com/upsidedownlabs/BioAmp-EXG-Pill)
[Getting Started](overview.md)

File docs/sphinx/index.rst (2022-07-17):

.. BioAmp-EXG-Pill Docs documentation master file, created by
   sphinx-quickstart on Thu Jun 23 14:12:08 2022.
   You can adapt this file completely to your liking, but it should at least
   contain the root `toctree` directive.

GIF-banner

|

..
    BioAmp EXG Pill documentation main file

.. _BioAmp-EXG-Pill-home:

BioAmp EXG Pill Documentation
##################################

|

.. toctree::
   :maxdepth: 2
   :caption: Contents:

   introduction/index.rst
   applications/index.rst
   software/index.rst
   hardware/index.rst

.. _Licensing:

License
*******

 +------------------------------------------------------------+----------------------------------------------------------+
 | 
 |   :width: 360px                                            |       :width: 265px                                      |
 |   :align: left                                             |       :align: left                                       |
 |   :alt: Licenses Facts                                     |       :alt: OSHWA Certificate                            |                     
 |                                                            |                                                          |                    
 |   Licenses Facts                                           |       OSHWA Certificate                                  |         
 |                                                            |                                                          |
 +------------------------------------------------------------+----------------------------------------------------------+

**Hardware**

CERN Open Hardware License Version 2 - Strongly Reciprocal `(CERN-OHL-S-2.0). <https://spdx.org/licenses/CERN-OHL-S-2.0.html>`_

.. _Licenses:

**Software**

MIT open source `license <http://opensource.org/licenses/MIT>`_

**Documentation:**

This work is licensed under a `Creative Commons Attribution 4.0 International License. <http://creativecommons.org/licenses/by/4.0/>`_

Documentation image

|

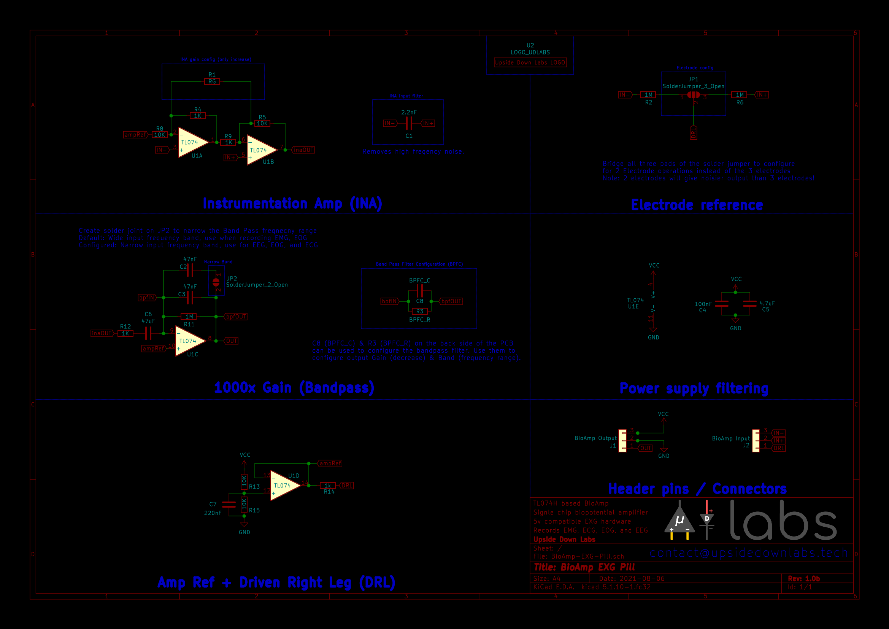
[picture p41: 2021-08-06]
graphics/docs/BioAmp-EXG-Pill-v1.0b-schematic-hc.png

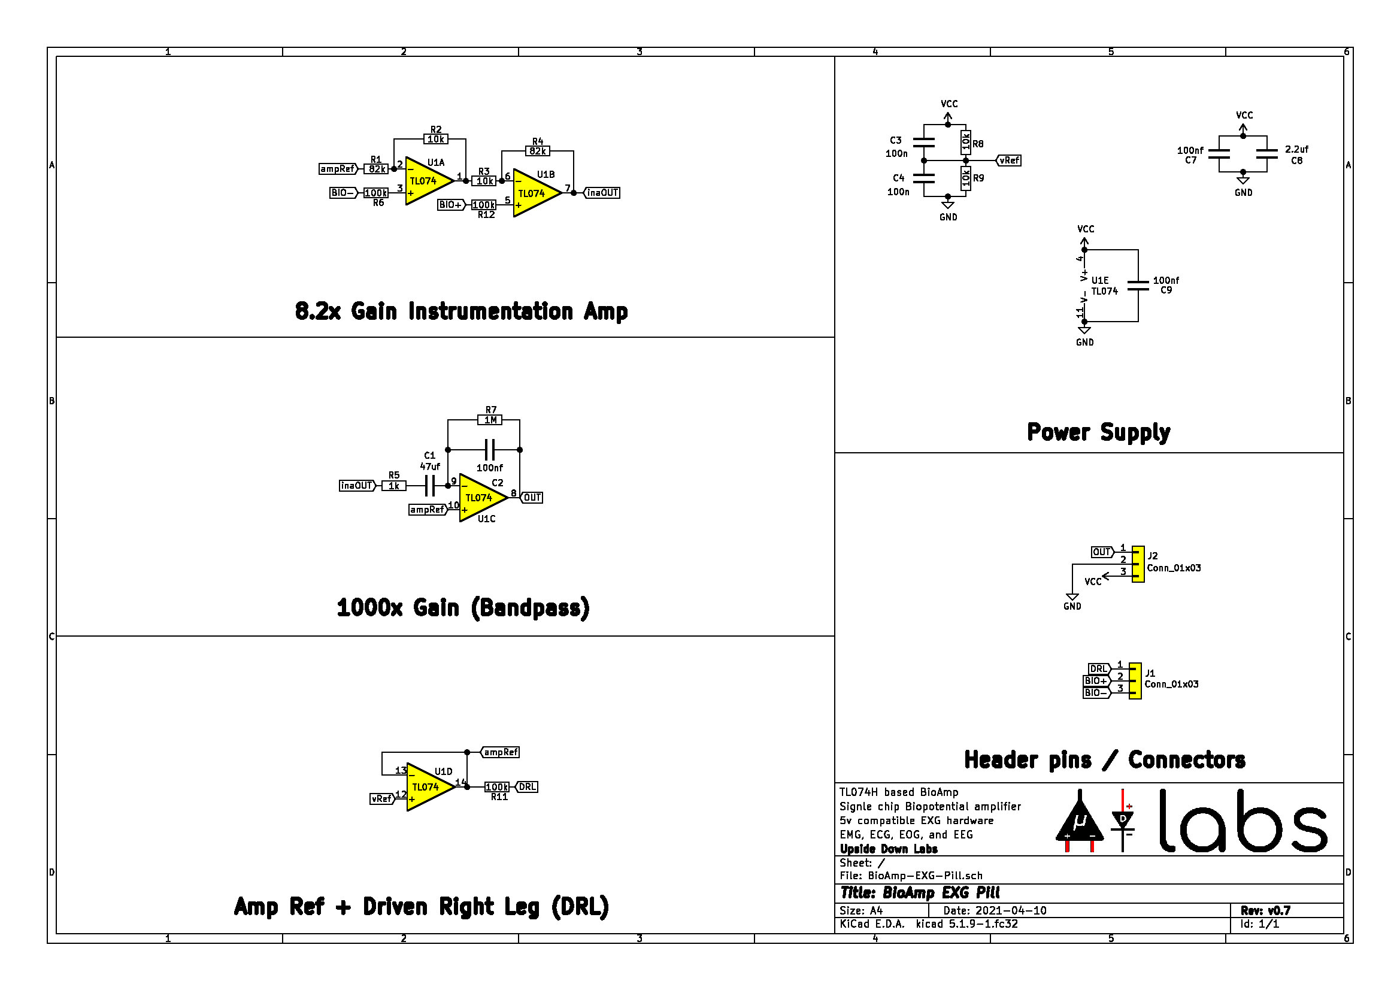
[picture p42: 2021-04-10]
graphics/docs/BioAmp-EXG-Pill-v0.7-schematic.png

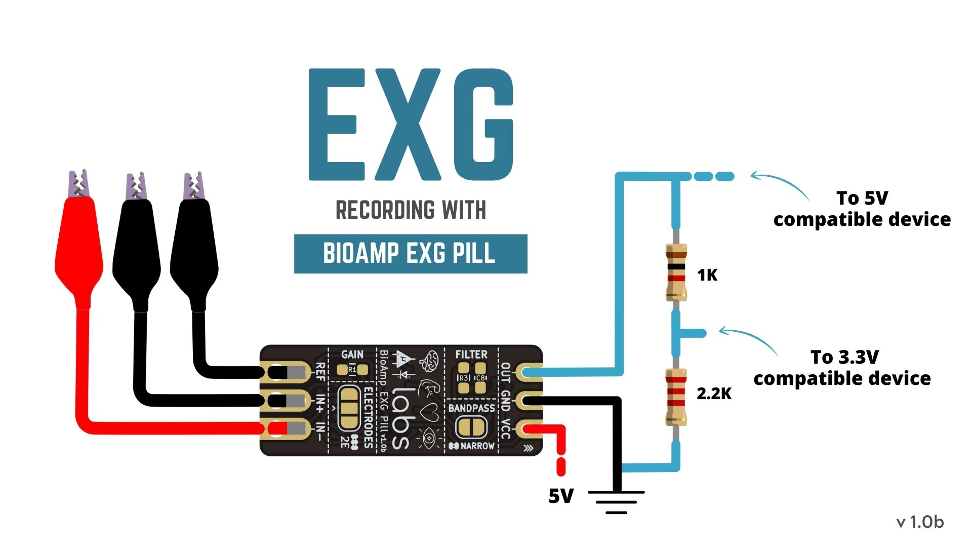
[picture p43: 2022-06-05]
docs/images/EXG-circuit/EXGRecording.jpg

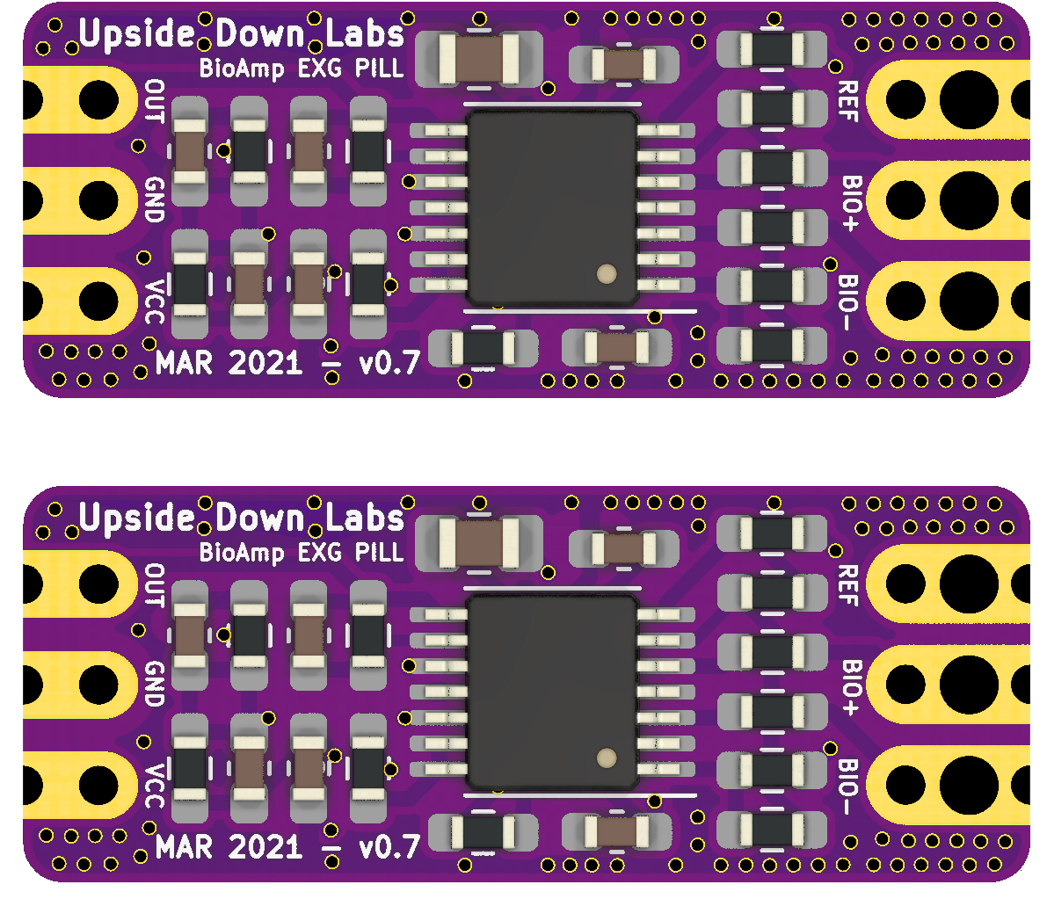
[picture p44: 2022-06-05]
docs/images/package/bioamp-exg-pill-render-explorer-pack.png

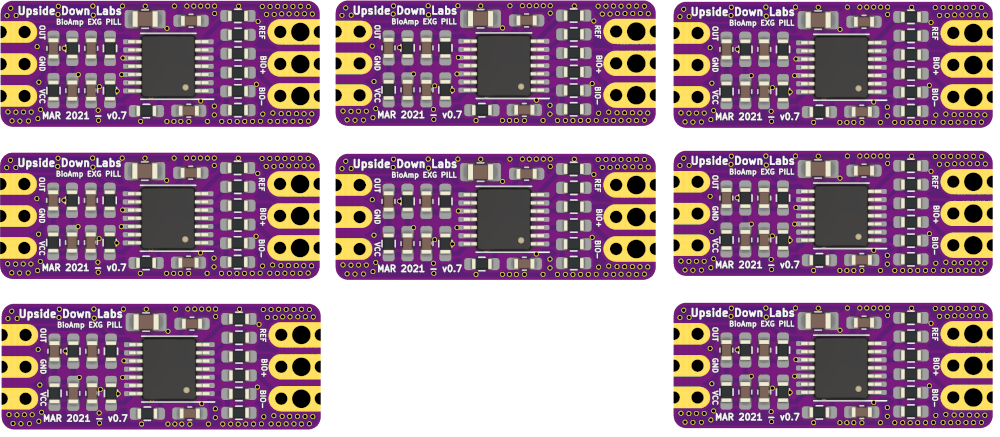
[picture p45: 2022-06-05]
docs/images/package/bioamp-exg-pill-render-neuroscience-ninja-pack.png

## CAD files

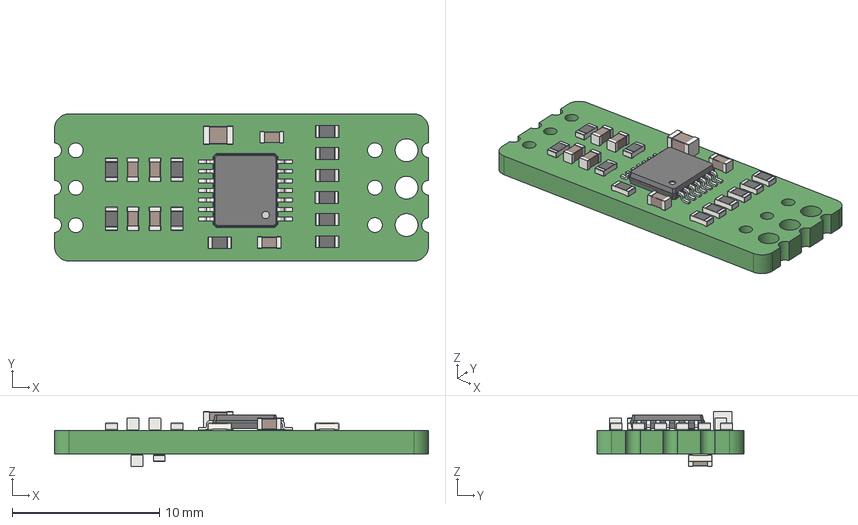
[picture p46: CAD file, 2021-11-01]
hardware/component/BioAmp-EXG-Pill.step
25.4 x 10.0 x 3.75 mm

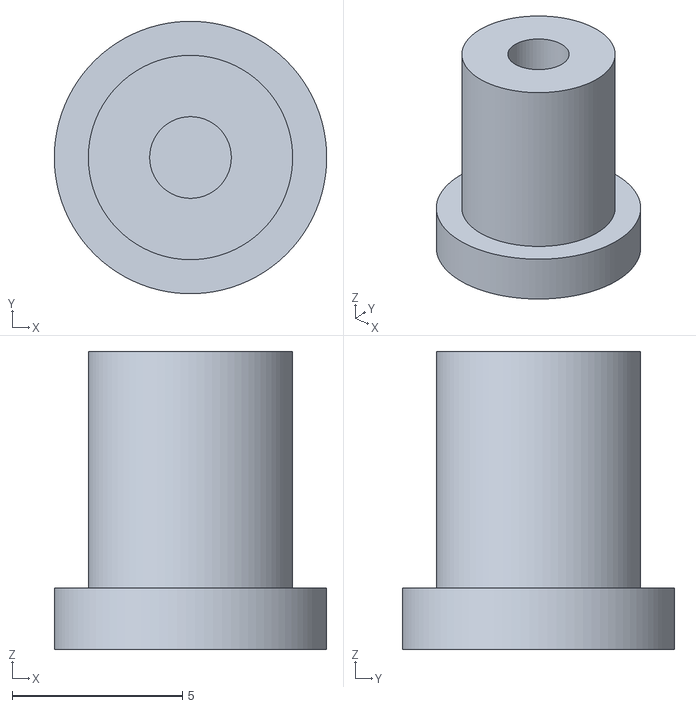
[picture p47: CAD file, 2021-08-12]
software/ClawController/3D-Claw/gear connector.stl
8.00 x 8.00 x 8.75

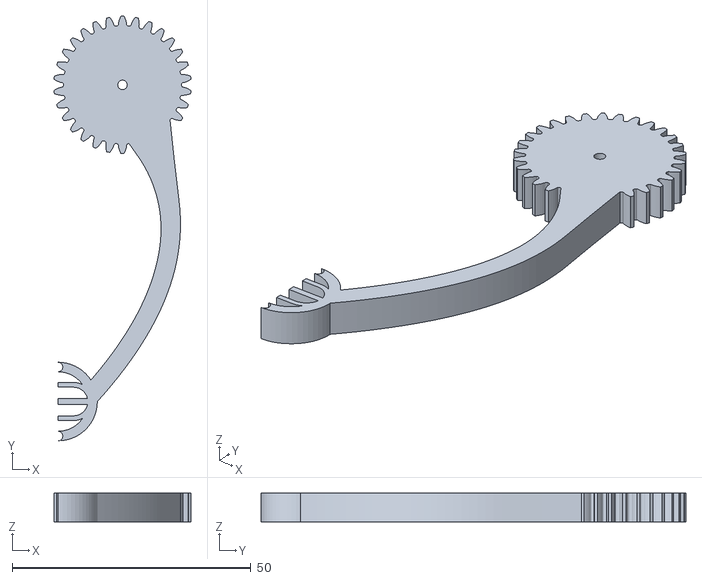
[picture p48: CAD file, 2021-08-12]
software/ClawController/3D-Claw/arm 2.stl
28.7 x 89.0 x 6.00

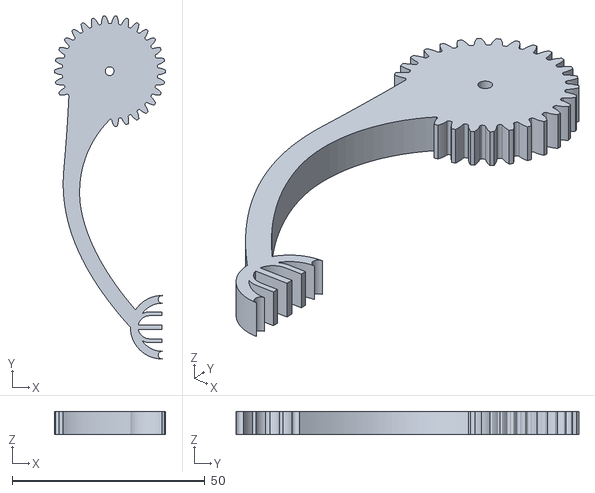
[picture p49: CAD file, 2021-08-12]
software/ClawController/3D-Claw/arm 1.stl
28.8 x 88.9 x 6.00

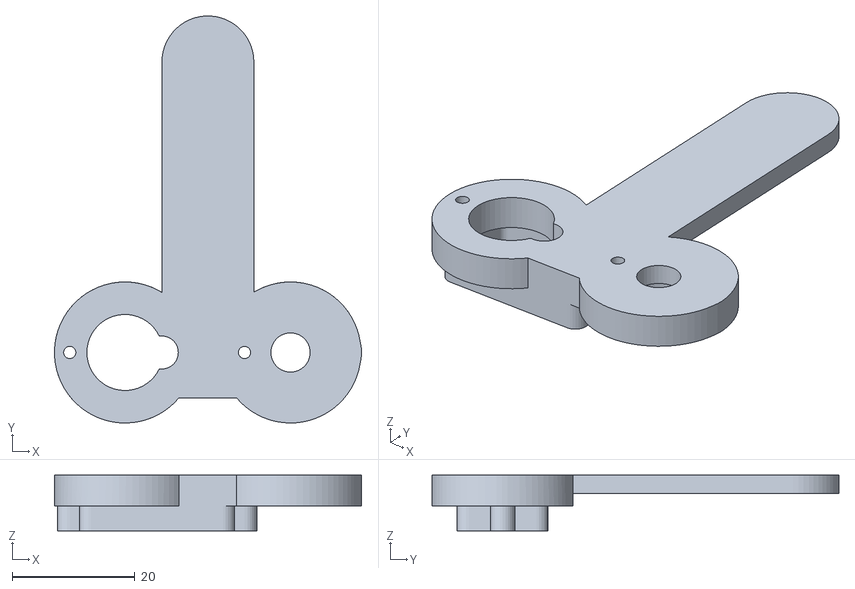
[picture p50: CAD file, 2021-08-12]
software/ClawController/3D-Claw/Base.stl
50.1 x 66.4 x 9.10

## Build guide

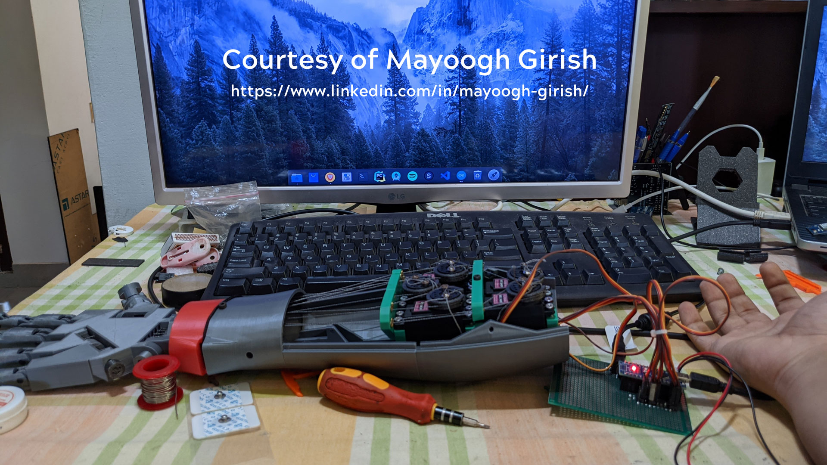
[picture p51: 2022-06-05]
docs/images/Mayoogh/Mayoogh-InMoov-arm-setup.jpg

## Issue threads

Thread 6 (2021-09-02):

### ISSUE TITLE
Blink detection is broken.

### ISSUE THREAD

**Issue by padmalaya-rawal** [upsidedownlabs/BioAmp-EXG-Pill#6]
Hey, thanks for providing such a great open source project. But just for your kind information the blink detection code is broken. : )

**Comment by padmalaya-rawal** [comment]
Hey, I tried the code once again and its working, that was my mistake. Closing the issue 👍🏻

**Comment by lorforlinux** [comment]
Hey @padmalaya-rawal, Thank you for your generous support.

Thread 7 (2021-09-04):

### ISSUE TITLE
[QUESTION] Bioelectrical impedance analysis (BIA) 

### ISSUE THREAD

**Issue by dmazzella** [upsidedownlabs/BioAmp-EXG-Pill#7]
Hi folks,
is possible to use BopAmp for bioimpecence analysis?

Thanks,
D.

**Comment by lorforlinux** [comment]
Hey @dmazzella, that is totally possible. BioAmp EXG Pill is basically a sophisticated amplifier for recording signals from the body. You can use the technique used in the [OpenBCI ganglion](https://github.com/OpenBCI/Ganglion_Hardware_Design_Files/blob/master/Ganglion_SCH.pdf) board for BIA.

**Comment by dmazzella** [comment]
Can you provide an example of use with BioAmp EXG Pill?

Thanks,
D.

**Comment by lorforlinux** [comment]
Hey @dmazzella, Please see the image below for a basic BIA setup. You can create a similar setup where BioAmp EXG Pill be the voltage measuring device connected to an ADC, then you create a constant current source. With these 2 building blocks in place, you have your own BIA setup ready. Also, checkout the [OpenBCI ganglion schematic](https://github.com/OpenBCI/Ganglion_Hardware_Design_Files/blob/master/Ganglion_SCH.pdf) to see how they are using INA and DAC for impedance detection. I hope this helps :)

![](https://www.researchgate.net/profile/Ehab-Mohamed-5/publication/301737400/figure/fig1/AS:366654107209728@1464428559601/Schematic-representation-of-the-bioelectric-impedance-analysis-BIA-measuring-technique.png)
Source: https://www.researchgate.net/figure/Schematic-representation-of-the-bioelectric-impedance-analysis-BIA-measuring-technique_fig1_301737400

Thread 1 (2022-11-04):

### ISSUE TITLE
Output dynamic range enhancement

### ISSUE THREAD

**Issue by daarshanik** [upsidedownlabs/BioAmp-EXG-Pill#1]
Hi
First of all., please accept my compliments for this excellent project.
---
I ran a few simulations for EXG pill schematic. I discovered that the output ranges from 2v to 3v. .. yeah it's not rail to rail..
Feeding this output directly to Arduino (10 bit ADC) , can lead to quite a few bits going unused .

As a solution, may be .., we can add a differential ADC directly onto EXG Pill board. 
I have MCP3301 and ATtuy85 in mind.
Cost wise both look similar., though I would personally prefer MCP3301 over ATTiny , because it offer extra 12bit accuracy.
your thoughts?

**Comment by lorforlinux** [comment]
Hey @optimistic-moron, I am glad you liked the project.

I do have plans to roll out a similar yet different project with ADS1115 and 4 x BioAmp (Circuit) on one board to provide a low-cost 4ch 16bit BioPotential amplification platform. Your idea of including the ADC on-board has crossed my mind before and I thought of using [ADC121S101](https://www.ti.com/product/ADC121S101#order-quality) but, that will increase the size, complexity, and cost of BioAmp EXG Pill that's why I didn't pursue it further.

The idea of BioAmp EXG Pill is to provide a robust analog front end that can be used with any 5v compatible ADC input. This brings unseen flexibility to the table and even if someone wants to create a 24bit BioPotential acquisition system using BioAmp EXG Pills they can use a chip like [ADS131M08](https://www.ti.com/product/ADS131M08?keyMatch=ADS131M08&tisearch=Search-EN-everything&usecase=GPN). I will be providing a KiCad template for the BioAmp EXG pill so that anybody can create custom boards. What are your thoughts on this?

Can you please share the simulation data here?
Also, I will be releasing the v1.0 circuit very soon, can you run the simulation for that circuit too?
It will be pretty much the same with very slight changes to further improve the BioAmp EXG Pill.

**Comment by optimistic-moron** [comment]
Hey @lorforlinux , thanks for your response.

ADS1115.., , I find the max sampling rate 860sps quite low ,esp. for EMG.
ADC121S101 , lacks differential mode , plus cost is high for a single channel.

ADS131M08 .. looks like a good choice.

Simulation data, i can add to a branch on the fork.
simulation on v1.0; shouldn't be a big deal either.

<b>eagerly awaiting v1.0 :)</b>

meanwhile, i am working on zero board (6.3 x 4 cm ) for v0.6 with provision for Attiny (purely because it was available locally).
Haven't tested yet. covid lockdown is delaying things. 
may be i can add schematic for that as well, to the same branch.

cheers!

**Comment by optimistic-moron** [comment]
Hey @lorforlinux 

Added simulation (ltspice) file at  https://github.com/optimistic-moron/BioAmp-EXG-Pill/tree/simulation/software/Simulation. 
Kindly review and let me know if this is OK.

Please also check if simulation results match with real hardware output?

thanks

**Comment by lorforlinux** [comment]
Hey @optimistic-moron, 

> ADS1115.., , I find the max sampling rate 860sps quite low ,esp. for EMG.

The sampling rate of 860sps shouldn't be a problem, I am using a sampling rate of 500Hz for the EMG right now and it works very well. See the demos below, code for both can be found in the software folder.
1. [ServoControl](https://www.youtube.com/watch?v=ZePE1umyzFI)
2. [LEDBarGraph](https://www.youtube.com/watch?v=MzLAFVXk7_M)

From various sources, I have seen that 20-300Hz is a very good range for sEMG usually getting peaks of 70-80Hz. The sEMG acquisition for research purposes requires at least 600Hz and 860Hz would work well I believe. What are your thoughts on this? 

Note: I have set the frequency response to ~75-150Hz with IIR filter in the Arduino EMG code. 

> ADS131M08 .. looks like a good choice.

Agreed, it provides the best price to performance ratio!

> eagerly awaiting v1.0 :)

Coming very very soon ;)

> meanwhile, i am working on zero board (6.3 x 4 cm ) for v0.6 with provision for Attiny

Great! 
Besides ATTiny85, Do you have the [TL074H](https://www.ti.com/product/TL074H) chip with you?

> may be I can add a schematic for that as well, to the same branch.

Yes, please share I'll help you improve it :)

> Added simulation (ltspice) file at ...

I think you need to update the TL074 model to [TL074H](https://www.ti.com/product/TL074H#design-development##design-tools-simulation). 
Also, can you can create a separate folder for simulation just like hardware/software.

If you are trying the circuit with TL074CD (dip package) then you might not get the desired result because it works on 7v (min). You require the updated TL074H from TI to make the circuit work on 5v. 

I can try to send you some samples to tinker with, please send us an email at contact@upsidedownlabs.tech
It's a bit difficult to ship anything due to lockdown right now :(

**Comment by optimistic-moron** [comment]
Awesome @lorforlinux ..., that was a really quick response :)

>From various sources, I have seen that 20-300Hz is a very good range for sEMG usually getting peaks of 70-80Hz. The sEMG acquisition for research purposes requires at least 600Hz and 860Hz would work well I believe. What are your thoughts on this?

This is a very good point you have brought up here. There are actually 2 reasons , why I am looking for high sampling frequency:

1. From the sources, i read some time back, the sEMG signal can reach upto 500Hz. If we recall [Nynquist Criteria](https://en.wikipedia.org/wiki/Nyquist_rate), the sampling frequency of 1Ksps { Fs>=2 x fm = 2x500Hz) would be helpful.

2. Higher sampling frequency can help me improve adc resolution by means of  [oversampling](https://en.wikipedia.org/wiki/Oversampling#Resolution).


> Besides ATTiny85, Do you have the [TL074H](https://www.ti.com/product/TL074H) chip with you?

Couldn't find TL074H offline/online(India). Factory lead time was also quite high on mouser. That's why took on TL074.

> I think you need to update the TL074 model to [TL074H](https://www.ti.com/product/TL074H#design-development##design-tools-simulation).
Again, wasn't getting the exact chip, so started with whatever was available. More to this in next response...


> If you are trying the circuit with TL074CD (dip package) then you might not get the desired result because it works on 7v (min). You require the updated TL074H from TI to make the circuit work on 5v.

In the simulation, using your exact schematic , if i replace the 5v input with 9v, then i see  the offset move from ~2.5v to ~4.5v. The voltage swing as well as dynamic range(~1v) look almost similar. Hence wanted to give it a try. 
Of-course form factor (pcb dimensions) and practicality (5v) wise TL074H shines.
 
> I can try to send you some samples to tinker with, please send us an email at [contact@upsidedownlabs.tech](mailto:contact@upsidedownlabs.tech)
> It's a bit difficult to ship anything due to lockdown right now :(

thankyou soo much for the offer :) . will ping you there.

Meanwhile, I am working on building an open source ultra low cost prosthetic hand project. Plan to start posting code on Github soon for this. I see  scope of collaboration there as well. 

thanks .

**Comment by lorforlinux** [comment]
>Couldn't find TL074H offline/online(India). Factory lead time was also quite high on mouser. That's why took on TL074.

I can send you some :)

> In the simulation, using your exact schematic , if i replace the 5v input with 9v, then i see the offset move from ~2.5v to ~4.5v. The voltage swing as well as dynamic range(~1v) look almost similar. Hence wanted to give it a try.

Yes, it should just work fine!

I have used TL074CD for [BioAmp v1.5](https://github.com/upsidedownlabs/BioAmp_v1.5) and it gives very good result when used with 9v battery.

> Meanwhile, I am working on building an open source ultra low cost prosthetic hand project. Plan to start posting code on Github soon for this. I see scope of collaboration there as well.

I do have a plan to create an stm32f103 based prostheric arm controller, we can surely collaborate!

**Comment by optimistic-moron** [comment]
> I do have a plan to create an stm32f103 based prostheric arm controller, we can surely collaborate!
how about [TM4C123GXL](https://www.ti.com/tool/EK-TM4C123GXL) instead? this one is cortex M4, with floating point support. Board is quite cheap.

**Comment by lorforlinux** [comment]
> how about TM4C123GXL instead? this one is cortex M4, with floating point support. Board is quite cheap.

Yes, That's also a good option. MSP432 is also very good In that regard.

**Comment by lorforlinux** [comment]
@daarshanik Hey, did you see the v0.9 schematic yet?
I have updated the design and it's getting closer to v1.0 slowly. 
Graphics has not been updated, please use KiCAD to see the design :)

**Comment by lorforlinux** [comment]
@daarshanik I have updated hardware files to v1.0a ;)

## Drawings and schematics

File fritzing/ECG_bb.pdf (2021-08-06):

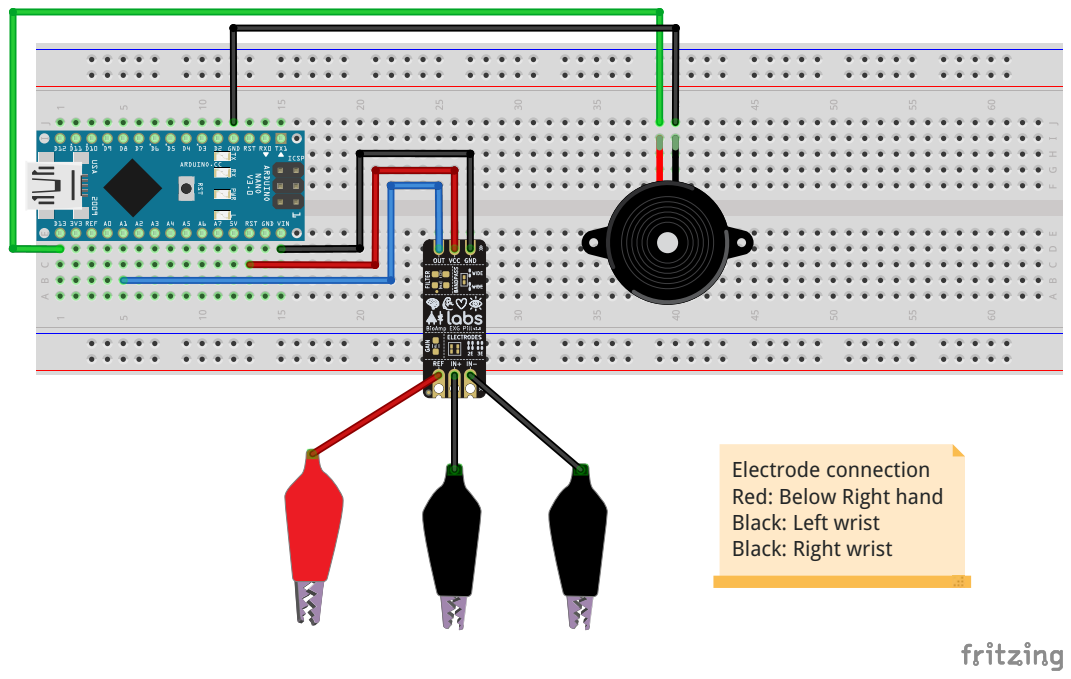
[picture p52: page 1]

Electrode connection
Red: Below Right hand
Black: Left wrist
Black: Right wrist

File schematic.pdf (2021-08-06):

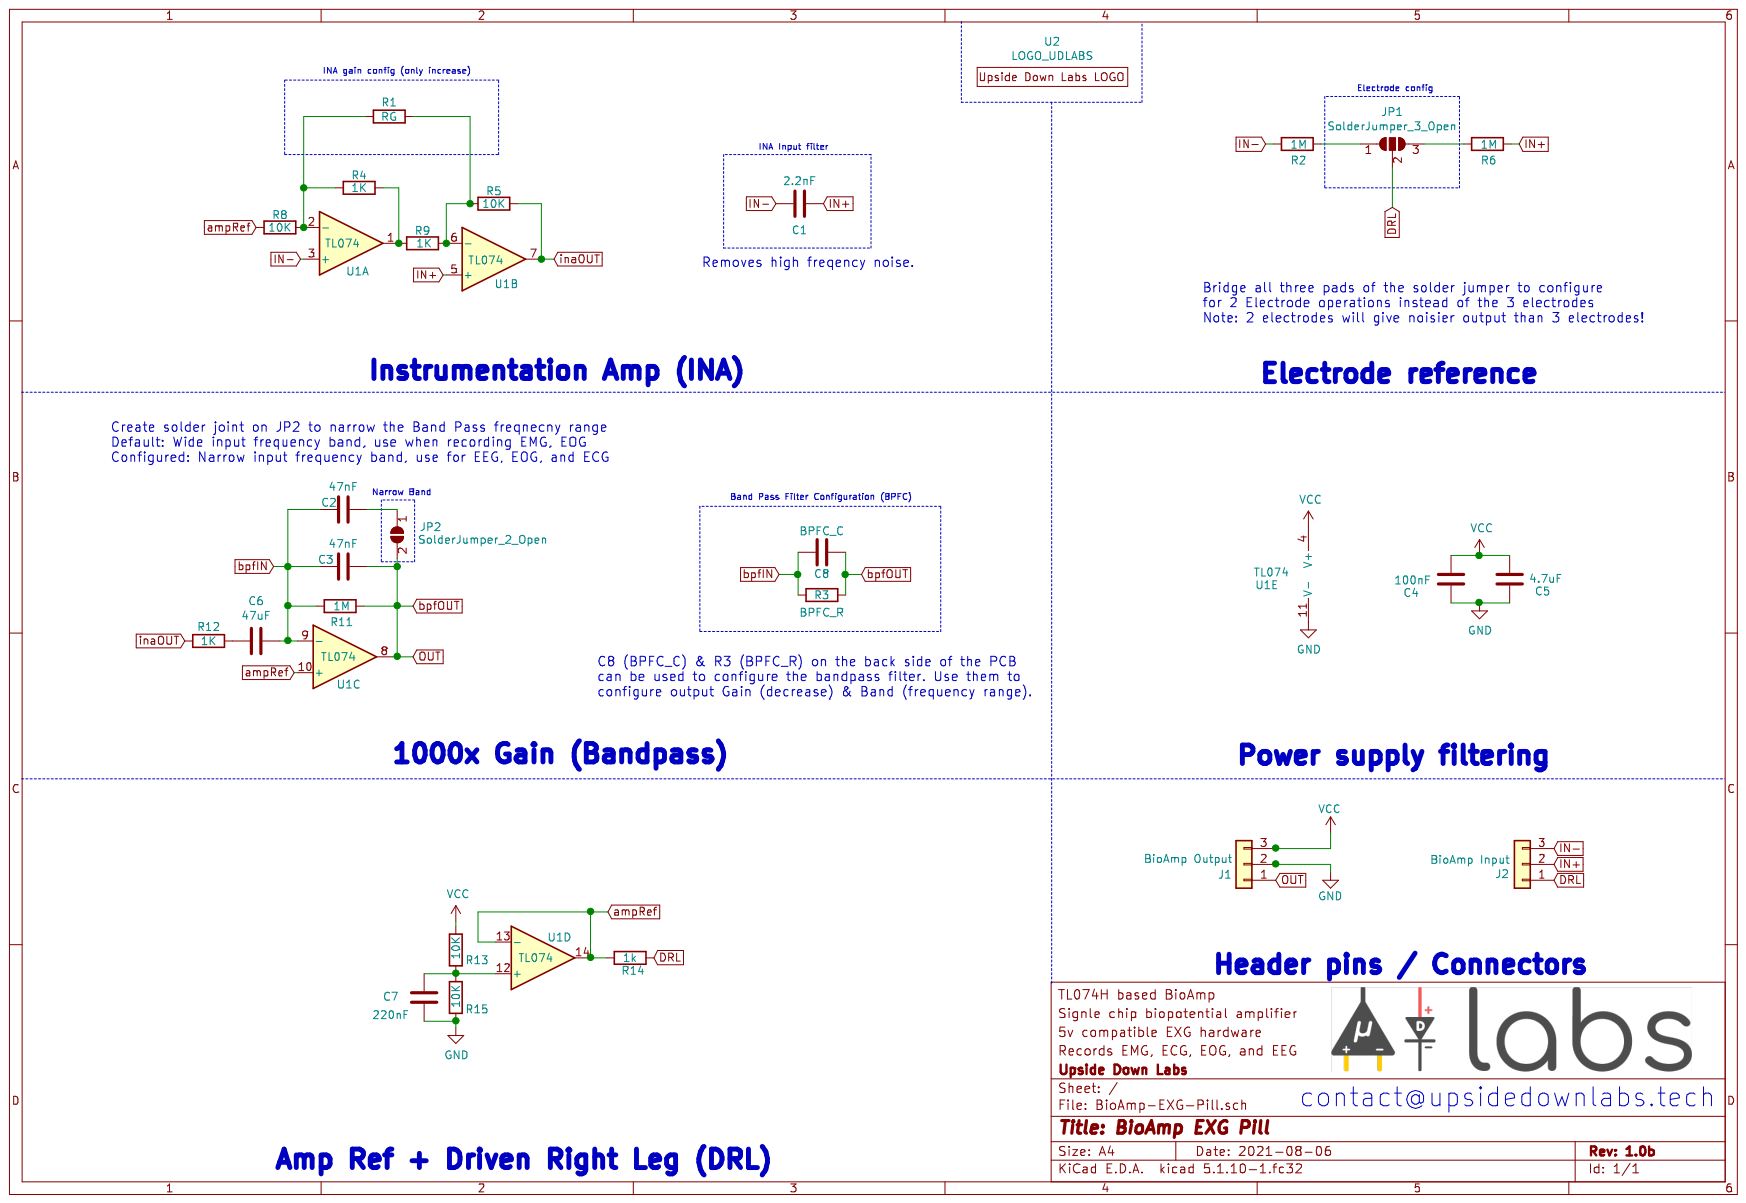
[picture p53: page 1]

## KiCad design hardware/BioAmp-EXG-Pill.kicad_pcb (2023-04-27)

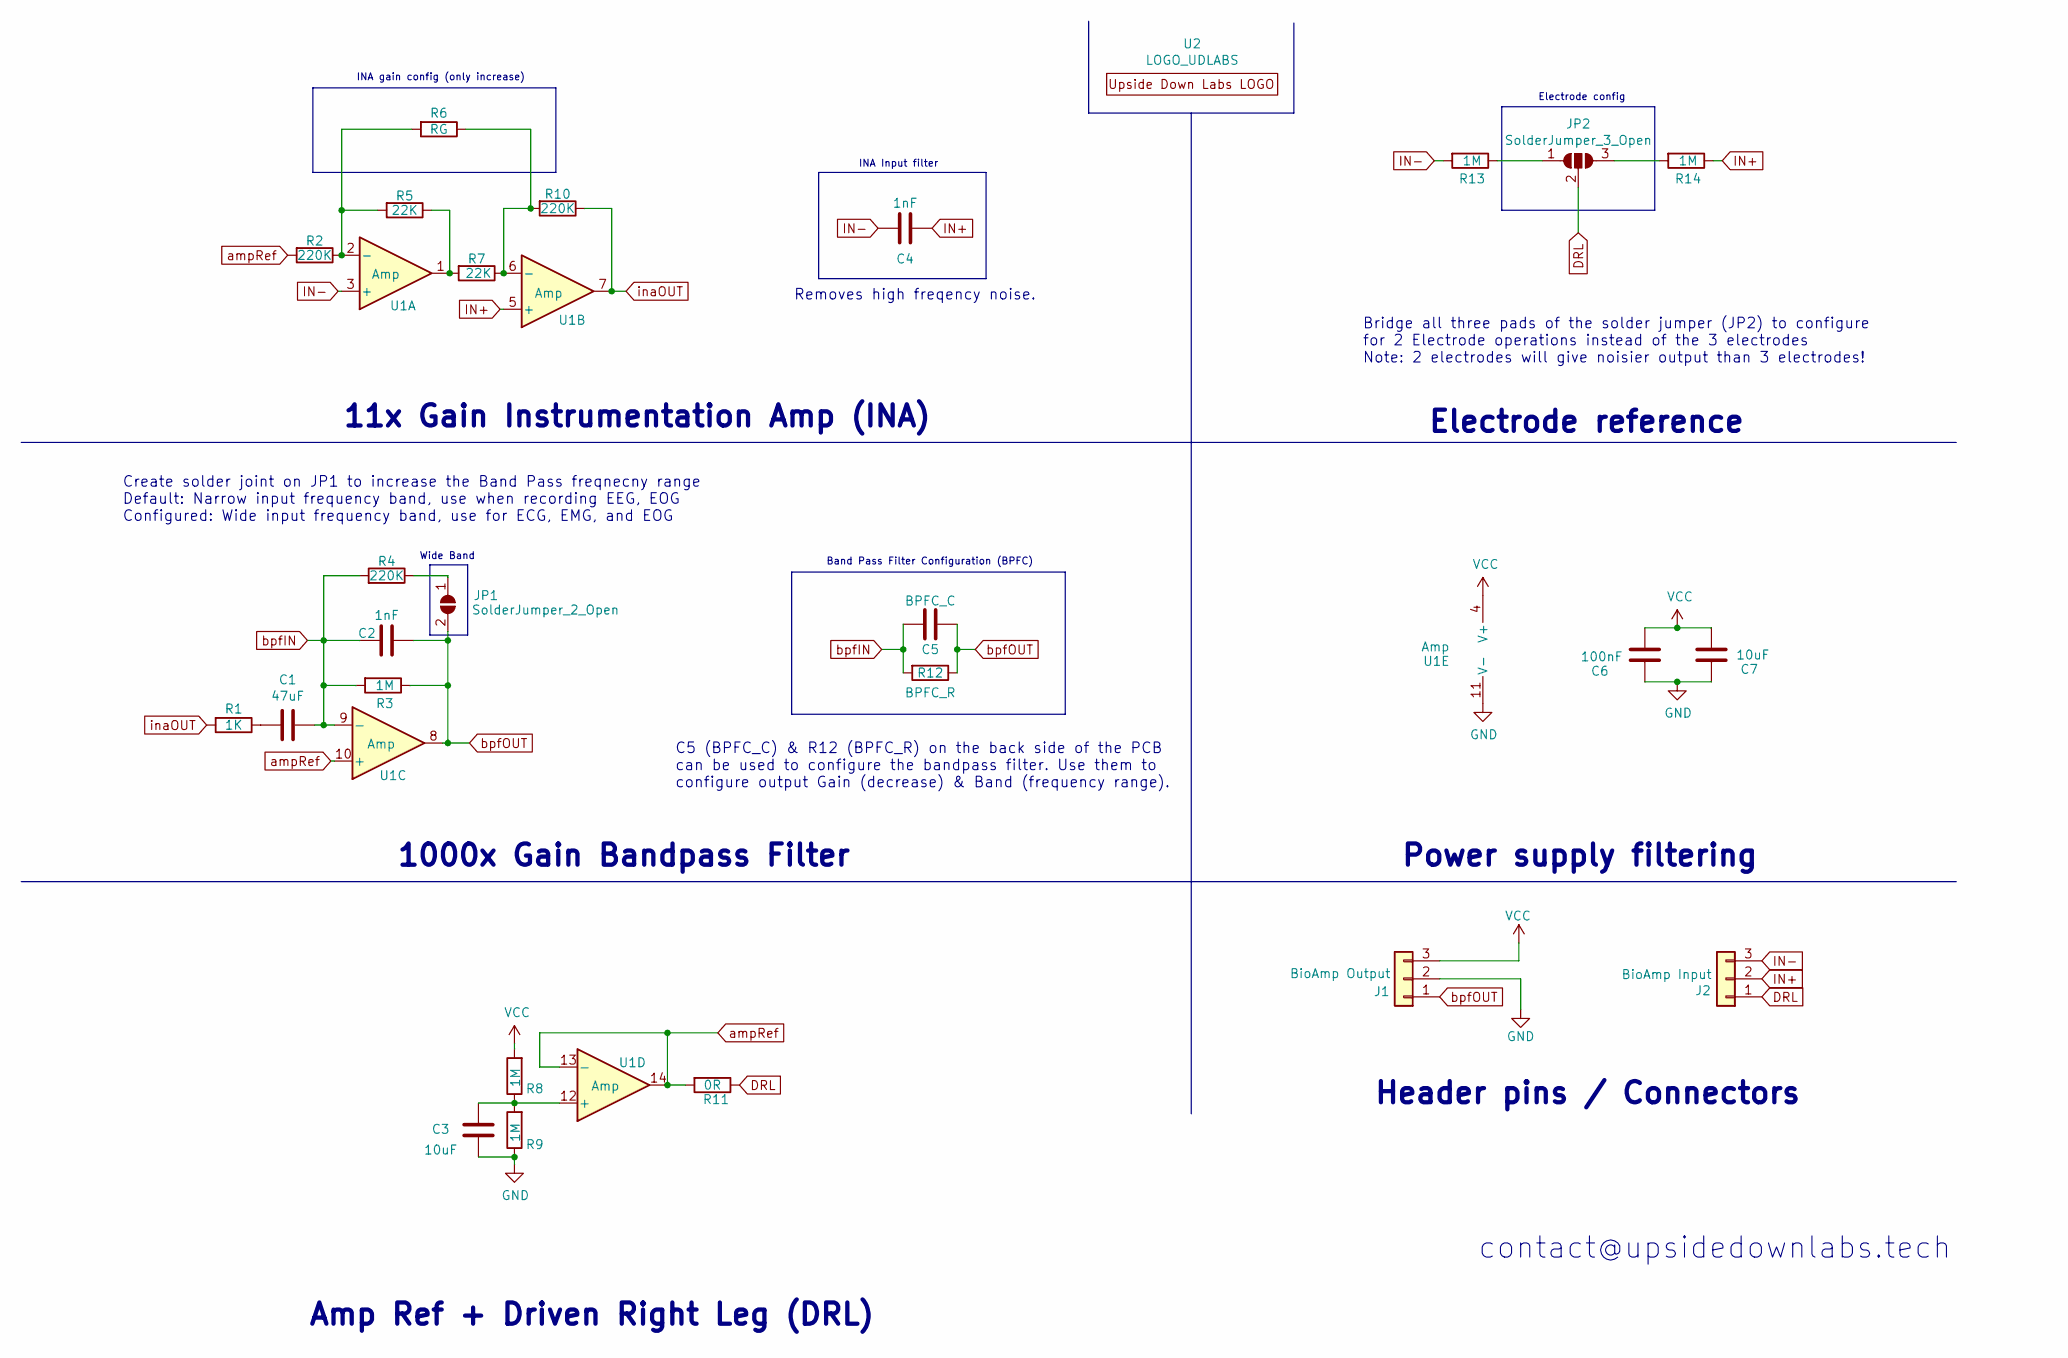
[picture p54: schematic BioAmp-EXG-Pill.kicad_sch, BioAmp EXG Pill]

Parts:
C1: 47uF; C_0805_2012Metric_Pad1.18x1.45mm_HandSolder
C2, C4: 1nF; C_0603_1608Metric_Pad1.08x0.95mm_HandSolder
C3, C7: 10uF; C_0603_1608Metric_Pad1.08x0.95mm_HandSolder
C5: BPFC_C; C_0603_1608Metric_Pad1.08x0.95mm_HandSolder
C6: 100nF; C_0603_1608Metric_Pad1.08x0.95mm_HandSolder
J1: BioAmp Output; PinHeader_1x03_P2.54mm_Vertical
J2: BioAmp Input; PinHeader_1x03_P2.54mm_Vertical
JP1: SolderJumper_2_Open; SolderJumper-2_P1.3mm_Open_RoundedPad1.0x1.5mm
JP2: SolderJumper_3_Open; SolderJumper-3_P1.3mm_Open_RoundedPad1.0x1.5mm
R1: 1K; R_0603_1608Metric_Pad0.98x0.95mm_HandSolder
R2, R4, R10: 220K; R_0603_1608Metric_Pad0.98x0.95mm_HandSolder
R3, R8, R9, R13, R14: 1M; R_0603_1608Metric_Pad0.98x0.95mm_HandSolder
R5, R7: 22K; R_0603_1608Metric_Pad0.98x0.95mm_HandSolder
R6: RG; R_0603_1608Metric_Pad0.98x0.95mm_HandSolder
R11: 0R; R_0603_1608Metric_Pad0.98x0.95mm_HandSolder
R12: BPFC_R; R_0603_1608Metric_Pad0.98x0.95mm_HandSolder
U1: Amp; TSSOP-14_4.4x5mm_P0.65mm
U2: LOGO_UDLABS; EXG

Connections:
DRL: J2.1, JP2.2 (C), R11.1; also elsewhere on the board
GND: C3.2, C6.1, C7.1, J1.2, R9.1, U1.11 (V-); also elsewhere on the board
IN+: C4.1, J2.2, R14.1, U1.5 (+); also elsewhere on the board
IN-: C4.2, J2.3, R13.2, U1.3 (+); also elsewhere on the board
unnamed: C1.2, R1.1
unnamed: C3.1, R8.1, R9.2, U1.12 (+)
unnamed: JP1.1 (A), R4.1
unnamed: JP2.1 (A), R13.1
unnamed: JP2.3 (B), R14.2
unnamed: R2.1, R5.2, R6.2, U1.2 (-)
unnamed: R5.1, R7.2, U1.1
unnamed: R6.1, R7.1, R10.2, U1.6 (-)
VCC: C6.2, C7.2, J1.3, R8.2, U1.4 (V+); also elsewhere on the board
ampRef: R2.2, R11.2, U1.10 (+), U1.13 (-), U1.14
bpfIN: C1.1, C2.2, C5.2, R3.2, R4.2, R12.2, U1.9 (-)
bpfOUT: C2.1, C5.1, J1.1, JP1.2 (B), R3.1, R12.1, U1.8; also elsewhere on the board
inaOUT: R1.2, R10.1, U1.7

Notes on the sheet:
contact@upsidedownlabs.tech
1000x Gain Bandpass Filter
Create solder joint on JP1 to increase the Band Pass freqnecny range Default: Narrow input frequency band, use when recording EEG, EOG Configured: Wide input frequency band, use for ECG, EMG, and EOG
Band Pass Filter Configuration (BPFC)
Electrode config
C5 (BPFC_C) & R12 (BPFC_R) on the back side of the PCB can be used to configure the bandpass filter. Use them to configure output Gain (decrease) & Band (frequency range).
Header pins / Connectors
11x Gain Instrumentation Amp (INA)
Bridge all three pads of the solder jumper (JP2) to configure for 2 Electrode operations instead of the 3 electrodes Note: 2 electrodes will give noisier output than 3 electrodes!
Power supply filtering
Amp Ref + Driven Right Leg (DRL)
Removes high freqency noise.
Wide Band
INA gain config (only increase)
Electrode reference
INA Input filter

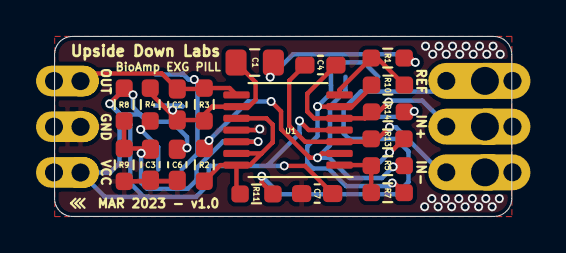
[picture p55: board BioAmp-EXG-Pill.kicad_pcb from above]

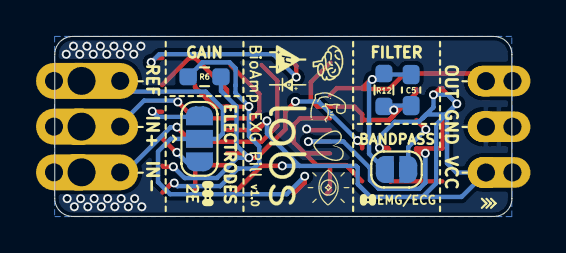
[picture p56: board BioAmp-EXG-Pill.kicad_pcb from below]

Board: 2 copper layers, 25.4 x 10.0 mm, 30 parts (6 on the bottom side), 17 nets.

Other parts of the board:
J1#2: BioAmp Output; PinHeader_1x03_P2.54mm_Vertical
J2#2, J2#3: BioAmp Input; PinHeader_1x03_P2.54mm_Vertical

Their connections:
DRL: J2#2.1, J2#3.1; also elsewhere on the board
GND: J1#2.2; also elsewhere on the board
IN+: J2#2.2, J2#3.2; also elsewhere on the board
IN-: J2#2.3, J2#3.3; also elsewhere on the board
VCC: J1#2.3; also elsewhere on the board
bpfOUT: J1#2.1; also elsewhere on the board

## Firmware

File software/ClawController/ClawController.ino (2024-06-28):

// Claw Controller - BioAmp EXG Pill
// https://github.com/upsidedownlabs/BioAmp-EXG-Pill

// Upside Down Labs invests time and resources providing this open source code,
// please support Upside Down Labs and open-source hardware by purchasing
// products from Upside Down Labs!

// Copyright (c) 2021 Upside Down Labs - contact@upsidedownlabs.tech

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
#include <inttypes.h>
#include <math.h>

#if defined(ESP32) 
  #include <ESP32Servo.h>
#else
  #include <Servo.h>
#endif

#define SAMPLE_RATE 500
#define BAUD_RATE 115200
#define INPUT_PIN A0
#define BUFFER_SIZE 128
#define SERVO_PIN 9
#define EMG_MIN 2
#define EMG_MAX 10
#define SERVO_MIN 90
#define SERVO_MAX 180

int circular_buffer[BUFFER_SIZE];
int32_t sum;
int data_index;
int flag=0;
Servo servo;

inline float mapf(float x, float in_min, float in_max, float out_min, float out_max) {
  return (x - in_min) * (out_max - out_min) / (in_max - in_min) + out_min;
}

void setup() {
  // Serial connection begin
  Serial.begin(BAUD_RATE);
  // Attach servo
  servo.attach(SERVO_PIN);
}

void loop() {
  //For initial setup only
  if(flag==0){
    Serial.print("Servo is now at ");
    Serial.print(SERVO_MAX);
    Serial.println(" degrees. Place the Servo arm & screw it in place.");
    Serial.println("It is recommended to remove USB while placing servo arm.");

    servo.write(SERVO_MAX); 
    delay(10 * 1000);  // 10 second pause
    flag=1;  
  }
  
  // Calculate elapsed time
  static unsigned long past = 0;
  unsigned long present = micros();
  unsigned long interval = present - past;
  past = present;

  // Run timer
  static long timer = 0;
  timer -= interval;

  // Sample and get envelop
  if(timer < 0) {
    timer += 1000000 / SAMPLE_RATE;
    int sensor_value = analogRead(INPUT_PIN);
    int signal = (int)EMGFilter((float)sensor_value);
    float envelop = getEnvelop(abs(signal));
    int servo_position = constrain((int)roundf(mapf(envelop,
                                                    EMG_MIN, EMG_MAX,
                                                    SERVO_MIN, SERVO_MAX)),
                                   SERVO_MIN, SERVO_MAX);
    servo.write(servo_position);
    Serial.print(signal);
    Serial.print(",");
    Serial.println(servo_position);
  }
}

// Envelop detection algorithm
float getEnvelop(int abs_emg){
  sum -= circular_buffer[data_index];
  sum += abs_emg;
  circular_buffer[data_index] = abs_emg;
  data_index = (data_index + 1) % BUFFER_SIZE;
  return (float(sum) / BUFFER_SIZE) * 2.0f;
}

// Band-Pass Butterworth IIR digital filter, generated using filter_gen.py.
// Sampling rate: 500.0 Hz, frequency: [74.5, 149.5] Hz.
// Filter is order 4, implemented as second-order sections (biquads).
// Reference: 
// https://docs.scipy.org/doc/scipy/reference/generated/scipy.signal.butter.html
// https://courses.ideate.cmu.edu/16-223/f2020/Arduino/FilterDemos/filter_gen.py
float EMGFilter(float input)
{
  float output = input;
  {
    static float z1, z2; // filter section state
    float x = output - 0.05159732*z1 - 0.36347401*z2;
    output = 0.01856301*x + 0.03712602*z1 + 0.01856301*z2;
    z2 = z1;
    z1 = x;
  }
  {
    static float z1, z2; // filter section state
    float x = output - -0.53945795*z1 - 0.39764934*z2;
    output = 1.00000000*x + -2.00000000*z1 + 1.00000000*z2;
    z2 = z1;
    z1 = x;
  }
  {
    static float z1, z2; // filter section state
    float x = output - 0.47319594*z1 - 0.70744137*z2;
    output = 1.00000000*x + 2.00000000*z1 + 1.00000000*z2;
    z2 = z1;
    z1 = x;
  }
  {
    static float z1, z2; // filter section state
    float x = output - -1.00211112*z1 - 0.74520226*z2;
    output = 1.00000000*x + -2.00000000*z1 + 1.00000000*z2;
    z2 = z1;
    z1 = x;
  }
  return output;
}

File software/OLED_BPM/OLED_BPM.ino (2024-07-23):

 // OLED_BPM - BioAmp EXG Pill
 // https://github.com/upsidedownlabs/BioAmp-EXG-Pill
 // https://github.com/upsidedownlabs/Heart-BioAmp-Arduino-Firmware

 // Upside Down Labs invests time and resources providing this open source code,
 // please support Upside Down Labs and open-source hardware by purchasing
 // products from Upside Down Labs!

 // Copyright (c) 2021 - 2024 Upside Down Labs - contact [at] upsidedownlabs.tech
 // Copyright (c) 2021 - 2024 Aryan Prakhar - aryanprakhar1010 [at] gmail.com
 // Copyright (c) 2021 - 2024 Dev Saran Sujan - devsaransujan [at] gmail.com

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
// Include necessary libraries
// By Adafruit
//https://github.com/adafruit/Adafruit_SSD1306/blob/master/Adafruit_SSD1306.h
//By Roberto Lo Giacco
// https://github.com/rlogiacco/CircularBuffer/blob/master/CircularBuffer.hpp

#include <Adafruit_SSD1306.h>
#include <Wire.h>
#include <math.h>
#include <CircularBuffer.hpp>

// Define constants for OLED display
#define OLED_Address 0x3C
#define SCREEN_WIDTH 128
#define SCREEN_HEIGHT 64
#define OLED_RESET -1

// Define constants for ECG sampling and processing
#define SAMPLE_RATE 125
#define BAUD_RATE 115200
#define INPUT_PIN A2
#define OUTPUT_PIN 13
#define DATA_LENGTH 16

// Initialize OLED display
Adafruit_SSD1306 display(SCREEN_WIDTH, SCREEN_HEIGHT, &Wire,-1);

// Global variables for BPM calculation
uint32_t avg = 0;
int data_index = 0;
bool peak = false;
int reading = 0;
uint8_t BPM = 0;
bool IgnoreReading = false;
bool FirstPulseDetected = false;
unsigned long FirstPulseTime = 0;
unsigned long SecondPulseTime = 0;
unsigned long PulseInterval = 0;

// Circular buffer to store pulse intervals
CircularBuffer<int,30> buffer;

void setup() {
  // Initialize serial communication
  Serial.begin(BAUD_RATE);
  
  // Set pin modes
  pinMode(INPUT_PIN, INPUT);
  pinMode(OUTPUT_PIN, OUTPUT);

  // Initialize OLED display
  if (!display.begin(SSD1306_SWITCHCAPVCC, OLED_Address)) {
    Serial.println(F("SSD1306 allocation failed"));
    for (;;);
  }

  // Set initial display settings
  display.clearDisplay();
  display.setTextSize(1);
  display.setTextColor(WHITE);
}

void loop() {
  // Calculate elapsed time since last loop
  static unsigned long past = 0;
  unsigned long present = micros();
  unsigned long interval = present - past;
  past = present;

  // Timer for maintaining consistent sampling rate
  static long timer = 0;
  timer -= interval;

  // Sample and process ECG signal at specified rate
  if(timer < 0){
    timer += 1000000 / SAMPLE_RATE;
    
    // Read sensor value and normalize
    float sensor_value = analogRead(INPUT_PIN);
    float signal = ECGFilter(sensor_value)/512;
    
    // Detect peaks in the signal
    peak = Getpeak(signal);
    
    // Blink LED on detected peak
    digitalWrite(OUTPUT_PIN, peak);

    // Process detected peaks for BPM calculation
    if(peak && IgnoreReading == false){
        if(FirstPulseDetected == false){
          FirstPulseTime = millis();
          FirstPulseDetected = true;
        }
        else{
          SecondPulseTime = millis();
          PulseInterval = SecondPulseTime - FirstPulseTime;
          buffer.unshift(PulseInterval);
          FirstPulseTime = SecondPulseTime;
        }
        IgnoreReading = true;
      }
      if(!peak){
        IgnoreReading = false;
      }  
      
      // Calculate and display BPM when buffer is full
      if (buffer.isFull()){
        // Calculate average pulse interval
        for(int i = 0 ;i < buffer.size(); i++){
          avg+=buffer[i];
        }
        avg=avg/ buffer.size();
        
        // Calculate BPM
        BPM = (1.0/avg) * 60.0 * 1000;
        avg = 0;
        buffer.pop();
        
        // Display BPM if it's within a reasonable range
        if (BPM < 240){
          Serial.print("BPM ");
          Serial.println(BPM);
          Serial.flush();
          
          // Update OLED display with new BPM
          display.clearDisplay();
          display.setTextSize(1);
          display.setCursor(24, 3);
          display.print("HEART_RATE(BPM): ");
          display.setCursor(50,26);
          display.setTextSize(3);
          display.println(BPM);
          display.display();
        }
      }  
  }
}

// Function to detect peaks in the ECG signal
bool Getpeak(float new_sample) {
  // DATA_LENGTH explanation:
    // This constant defines the size of the sliding window used for peak detection.
    // It determines how many recent samples are considered when calculating the mean 
    // and standard deviation of the signal. A larger value provides more stable 
    // detection but may introduce more lag.
  // Buffers for data, mean, and standard deviation
  static float data_buffer[DATA_LENGTH];
  static float mean_buffer[DATA_LENGTH];
  static float standard_deviation_buffer[DATA_LENGTH];
  
  // Check for peak
  // A peak is detected if the new sample exceeds the mean by more than 
  // half the DATA_LENGTH times the standard deviation
  if (new_sample - mean_buffer[data_index] > (DATA_LENGTH/2) * standard_deviation_buffer[data_index]) {
    data_buffer[data_index] = new_sample + data_buffer[data_index];
    peak = true;
  } else {
    data_buffer[data_index] = new_sample;
    peak = false;
  }

  // Calculate mean
  float sum = 0.0, mean, standard_deviation = 0.0;
  for (int i = 0; i < DATA_LENGTH; ++i){
    sum += data_buffer[(data_index + i) % DATA_LENGTH];
  }
  mean = sum/DATA_LENGTH;

  // Calculate standard deviation
  for (int i = 0; i < DATA_LENGTH; ++i){
    standard_deviation += pow(data_buffer[(i) % DATA_LENGTH] - mean, 2);
  }

  // Update mean buffer
  mean_buffer[data_index] = mean;

  // Update standard deviation buffer
  standard_deviation_buffer[data_index] =  sqrt(standard_deviation/DATA_LENGTH);

  // Update data_index
  data_index = (data_index+1)%DATA_LENGTH;

  // Return peak
  return peak;
}

// Band-Pass Butterworth IIR digital filter for ECG signal
// Sampling rate: 125.0 Hz, frequency range: [0.5, 44.5] Hz
// Filter is order 4, implemented as second-order sections (biquads)
float ECGFilter(float input)
{
  float output = input;
  {
    static float z1, z2; // filter section state
    float x = output - 0.70682283*z1 - 0.15621030*z2;
    output = 0.28064917*x + 0.56129834*z1 + 0.28064917*z2;
    z2 = z1;
    z1 = x;
  }
  {
    static float z1, z2; // filter section state
    float x = output - 0.95028224*z1 - 0.54073140*z2;
    output = 1.00000000*x + 2.00000000*z1 + 1.00000000*z2;
    z2 = z1;
    z1 = x;
  }
  {
    static float z1, z2; // filter section state
    float x = output - -1.95360385*z1 - 0.95423412*z2;
    output = 1.00000000*x + -2.00000000*z1 + 1.00000000*z2;
    z2 = z1;
    z1 = x;
  }
  {
    static float z1, z2; // filter section state
    float x = output - -1.98048558*z1 - 0.98111344*z2;
    output = 1.00000000*x + -2.00000000*z1 + 1.00000000*z2;
    z2 = z1;
    z1 = x;
  }
  return output;
}

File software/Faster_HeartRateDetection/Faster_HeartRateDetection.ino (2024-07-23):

// Faster_HeartRateDetection - BioAmp EXG Pill
// https://github.com/upsidedownlabs/BioAmp-EXG-Pill
// https://github.com/upsidedownlabs/Heart-BioAmp-Arduino-Firmware

// Upside Down Labs invests time and resources providing this open source code,
// please support Upside Down Labs and open-source hardware by purchasing
// products from Upside Down Labs!

// Copyright (c) 2021 - 2024 Upside Down Labs - contact [at] upsidedownlabs.tech
// Copyright (c) 2021 - 2024 Aryan Prakhar - aryanprakhar1010 [at] gmail.com
// Copyright (c) 2021 - 2024 Dev Saran Sujan - devsaransujan [at] gmail.com

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
#include <math.h>

// Define constants
#define SAMPLE_RATE 125       // Sampling rate in Hz
#define BAUD_RATE 115200      // Serial communication baud rate
#define INPUT_PIN A2          // Analog  pin for ECG signal
#define OUTPUT_PIN 13         // Digital output pin for LED
#define DATA_LENGTH 26        // Length of data buffer for peak detection
#define buffer_size 5         // Size of circular arrays for BPM calculation

// Global variables for BPM calculation
int data_index = 0;
uint32_t tdiff = 0;           // Time difference between consecutive peaks
uint8_t bpm = 0;              // Calculated Beats Per Minute

// Circular arrays for BPM calculation
int timeBuffer_index = -1;
int sumBuffer_index = -1;
uint32_t timeBuffer[buffer_size] = {0};
uint32_t sumBuffer[buffer_size] = {0};

// Variables for BPM calculation
uint32_t previous_time = 0;
uint32_t sum = 0;
uint32_t average = 0;

// Variables for peak detection and debouncing
unsigned long lastPeakStartTime = 0;
unsigned long peakCooldownPeriod = 2; // Cooldown period in milliseconds
bool isPeakActive = false;
bool peakEvent = false;

void setup() {
  // Initialize serial communication
  Serial.begin(BAUD_RATE);
  // Set pin modes
  pinMode(INPUT_PIN, INPUT);
  pinMode(OUTPUT_PIN, OUTPUT);
}

void loop() {
  // Calculate elapsed time since last loop
  static unsigned long past = 0;
  unsigned long present = micros();
  unsigned long interval = present - past;
  past = present;

  // Timer for maintaining consistent sampling rate
  static long timer = 0;
  timer -= interval;

  // Sample and process ECG signal at specified rate
  if(timer < 0){
    timer += 1000000 / SAMPLE_RATE;
    
    // Read sensor value and normalize
    float sensor_value = analogRead(INPUT_PIN);
    float signal = ECGFilter(sensor_value)/512;
    
    // Detect peaks in the signal
    peakEvent = Getpeak(signal);

    // Blink LED on detected peak
    digitalWrite(OUTPUT_PIN, peakEvent);

    // Calculate BPM when a peak is detected
    if(peakEvent){
      // Update time buffer for peak timing
      if(timeBuffer_index == -1){
        timeBuffer_index = (timeBuffer_index + 1) % buffer_size;
        timeBuffer[timeBuffer_index] = micros();
      }
      else{
        previous_time = timeBuffer[timeBuffer_index];
        timeBuffer_index = (timeBuffer_index + 1) % buffer_size;
        timeBuffer[timeBuffer_index] = micros();
        tdiff = timeBuffer[timeBuffer_index] - previous_time;
      }
    
      // Calculate BPM using circular arrays
      if(sumBuffer_index == -1){
        sumBuffer_index = (sumBuffer_index + 1) % buffer_size;
      }
      else{
        if(sumBuffer[sumBuffer_index] == 0){
          sumBuffer[sumBuffer_index] = tdiff;
          sum = sum + sumBuffer[sumBuffer_index];
          sumBuffer_index = (sumBuffer_index + 1) % buffer_size;
        }
        else{
          sum = sum - sumBuffer[sumBuffer_index];
          sumBuffer[sumBuffer_index] = tdiff;
          sum = sum + sumBuffer[sumBuffer_index];
          sumBuffer_index = (sumBuffer_index + 1) % buffer_size;
          average = sum / buffer_size;
          bpm = (60 * 1000000) / average;
          Serial.print("BPM : ");
          Serial.println(bpm);
        }
      }
    }
  }
}
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

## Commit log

2021-01-27 add back image of board
2021-01-27 add front image of board
2021-01-27 add board dimensions image
2021-01-27 add KiCAD files
    KiCAD project files for BioAmp EMG Pill v0.1
    [BioAmp-EMG-Pill.kicad_pcb, BioAmp-EMG-Pill.sch]
2021-02-12 Update to v0.5
    Tested circuit, working great!
    [BioAmp-EMG-Pill.kicad_pcb, BioAmp-EMG-Pill.sch]
2021-02-12 Update images to v0.5 board
2021-02-18 Update to v0.6
    [BioAmp-EMG-Pill.kicad_pcb, BioAmp-EMG-Pill.sch]
2021-03-12 update PCB
    [BioAmp-EMG-Pill.kicad_pcb, BioAmp-EMG-Pill.sch]
2021-04-10 Cleanup for EXG Pill
    Removing unnecessary files form BioAmp EMG Pill (v0.6) before pushing BioAmp EXG Pill (v0.7) files.
    [BioAmp-EMG-Pill.kicad_pcb, BioAmp-EMG-Pill.sch]
2021-04-10 KiCAD files BioAmp EXG Pill v0.7
    KiCAD (5.1.9) files for Upside Down Labs BioAmp EXG Pill v0.7
    [BioAmp-EXG-Pill.kicad_pcb, BioAmp-EXG-Pill.sch]
2021-04-10 BioAmp EXG panel gerbers
    These are the gerber files for BioAmp EXG Panel, which provides 21 BioAmp EXG Pill on a single PCB.
    [BioAmp-EXG-Panel-B_Cu.gbr, BioAmp-EXG-Panel-B_Mask.gbr, BioAmp-EXG-Panel-B_Paste.gbr, BioAmp-EXG-Panel-Edge_Cuts.gbr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]
2021-04-10 ZIP: BioAmp EXG panel gerbers
    ZIP of the gerber files for BioAmp EXG Panel, which provides 21 BioAmp EXG Pill on a single PCB.
2021-04-10 BioAmp EXG pill gerbers
    These are the gerber files for BioAmp EXG Pill v0.7
    [BioAmp-EXG-Pill-B_Cu.gbr, BioAmp-EXG-Pill-B_Mask.gbr, BioAmp-EXG-Pill-B_Paste.gbr, BioAmp-EXG-Pill-B_SilkS.gbr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]
2021-04-10 KiCAD: BioAmp EXG Panel
    KiCAD files for BioAmp EXG Panel which provides 21 BioAmp EXG Pills on a signale PCB.
2021-04-10 Assembled: BioAmp EXG Pill v0.7
    This image shows size comparision of the BioAmp EXG Pill v0.7 with a 2 rupee coin.
2021-04-18 Update Readme
    Include OSH Park shared PCB link
2021-04-30 EEG Filter
    Arduino code for recording EEG using BioAmp EXG Pill.
2021-04-30 Frequency response graph
    EEG Filter frequency reponse graph.
2021-05-01 add ECGFilter code
    This code is useful for filtering ECG signal sampled with BioAmp EXG pill. This is not required under normal circumstances as the raw output from EXG Pill is very clean as it is :)
2021-05-02 Recorded ECG image
    Sample ECG recorded with EXG Pill with ECGFilter program.
2021-05-02 add EMGFilter code
    This code is useful for filtering EMG signal sampled with BioAmp EXG pill.
2021-05-02 add EOGFilter code
    This code is useful for filtering EOG signal sampled with BioAmp EXG pill.
2021-05-13 add EMG Envelop detection code
    This is an Arduino example code for EMG signal filtering and evelop detection. Code can be used to control servo motor and display EMG strength on LED bar graph.
2021-05-13 EMG Envelop detection demo video
    This video shows the running EMG and it's envelop detected with the help of EMGEnvelop.ino Arduino code.
2021-05-13 EMG Envelop image
    This static image shows the EMG Envelop detected with EMGEnvelop.ino Arduino code.
2021-05-13 EMG wave image
    This image shows the EMG wave recorded with EMGFilter.ino Arduino code.
2021-05-13 LED bar graph code
    This code is to create a LED bar graph of EMG potential using BioAmp EXG Pill.
2021-05-16 Add servo control code
    This arduino code can be used to control a servo motor using EXG Pill.
2021-05-23 Update Readme
    added crowd supply banner, updated pills, and included software section with links to all the Arduino examples with a to-do list.
2021-05-23 Update Readme
    Fix EEG filter frequency text.
2021-05-24 Heart Beat Detection code
    This code detects heart beats and reflect them on Builtin LED of the Arduino board. The origianl ECG signal and the detected beat can also be seen on the Arduino serial plotter.
2021-05-24 HeartBeatDetection.ino serial plotter image
    This image shows the original ECG signal and detected beats on arduino serial plotter with HeartBeatDetection.ino code.
2021-06-20 BioAmp EXG Pill v0.9 KiCAD PCB
    [BioAmp-EXG-Pill.kicad_pcb]
2021-06-20 BioaAmp EXG Pill v0.9 KiCAD schematic
    [BioAmp-EXG-Pill.sch]
2021-06-24 Update v0.9 PCB silk screen
    [BioAmp-EXG-Pill.kicad_pcb]
2021-06-24 Update v0.9 schematic part values
    [BioAmp-EXG-Pill.sch]
2021-06-25 Update v0.9 PCB
    [BioAmp-EXG-Pill.kicad_pcb]
2021-06-26 BioAmp EXG Pill v1.0 alpha schematic
    This version of the BioAmp EXG Pill is near to the final release version (v1.0) for the Crowd Supply campaign.
    [BioAmp-EXG-Pill.sch]
2021-06-26 BioAmp EXG Pill v1.0 alpha PCB
    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
    [BioAmp-EXG-Pill.kicad_pcb]
2021-08-06 Repo cleanup
    Re-arranging all the files and folders for better accessibility.
    [BioAmp-EXG-Panel-B_Cu.gbr, BioAmp-EXG-Panel-B_Mask.gbr, BioAmp-EXG-Panel-B_Paste.gbr, BioAmp-EXG-Panel-Edge_Cuts.gbr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]
2021-08-06 BioAmp EXG Pill v1.0b KiCAD files
    This is the Beta version of the BioAmp EXG Pill v1.0 with updated power pinout, solder jumpers and more.
    [BioAmp-EXG-Pill.kicad_pcb, BioAmp-EXG-Pill.sch]
2021-08-06 EXG PCB marking
2021-08-06 Fully assembled v0.7
2021-08-06 v1.0a board svg
2021-08-06 v0.7 PCB
2021-08-06 Experimental: Fritzing files
    [ECG.fzz, EMG-Bar-Graph.fzz]
2021-08-06 v1.0b front PCB
2021-08-12 Servo claw controller sketch (#5)
    * Claw controller sketch
    This is a demo sketch for controlling claw, it is based on servo controller sketch.
    * Update readme
    Updated software examples list with new Claw Controller sketch
    * 3D printable claw
    Including 3D printing files of claw and an image
    [Base.stl, arm 1.stl, arm 2.stl, gear connector.stl]
2021-08-22 Claw Controller sketch
    This updated Claw Controller code now works for Arduino UNO/NANO, ESP32, and other development boards.
2021-08-22 Drowsiness Detection sketch
    This updated Drowsiness Detection code now works for Arduino UNO/NANO, ESP32, and other development boards.
2021-08-22 ECG Filter sketch
    This updated ECG Filter code now works for Arduino UNO/NANO, ESP32, and other development boards.
2021-08-22 EEG Filter sketch
    This updated EEG Filter code now works for Arduino UNO/NANO, ESP32, and other development boards.
2021-08-22 EMG Envelop sketch
    This updated EMG Envelop code now works for Arduino UNO/NANO, ESP32, and other development boards.
2021-08-22 EMG Filter sketch
    This updated EMG Filter code now works for Arduino UNO/NANO, ESP32, and other development boards.
2021-08-22 EOG Filter sketch
    This updated EOG Filter code now works for Arduino UNO/NANO, ESP32, and other development boards.
2021-08-22 Eye Blink Detection sketch
    This updated Eye Blink Detection code now works for Arduino UNO/NANO, ESP32, and other development boards.
2021-08-22 Fixed Sampling sketch
    This updated Fixed Sampling code now works for Arduino UNO/NANO, ESP32, and other development boards.
2021-08-22 Heart Beat Detection sketch
    This updated Heart Beat Detection code now works for Arduino UNO/NANO, ESP32, and other development boards.
2021-08-22 LED Bar Graph sketch
    This updated LED Bar Graph Detection code now works for Arduino UNO/NANO, ESP32, and other development boards.
2021-08-22 Servo Control sketch
    This updated Servo Control code now works for Arduino UNO/NANO, ESP32, and other development boards.
2021-08-27 BioAmp EXG PIll with Arduino Nano
    Basic circuit of BioAmp EXG Pill with Arduino nano for recording EMG, ECG, EOG, and EEG.
2021-08-27 Circuit for EMG
    Ulnar nerve connection with BioAmp EXG Pill for EMG recording.
2021-09-04 EOG based Photo Capture through BLE
    This program uses ESP32 BLE Keyboard functionality to capture photo by detecting eye blinks.
2021-09-04 Basic Circuit
    Basic circuit of BioAmp EXG Pill with Arduino Nano.
2021-09-04 Update readme
    Updated readme with circuits.
2021-09-05 Electrocardiography (Hand EKG) circuit
2021-09-14 EOG electrode placements
2021-11-01 Kicad Schematic Symbol and Footprint for BioAmp-EXG-Pill (#11)
    * Added footprint for BioAmp-EXG-Pill Module
    * Made Footprint and schematic sybols for BioAmp-EXG-Pill module
    * Added Footprint and Symbol libraries for BioAmp-EXG-Pill module
    * Footprint and Symbol libraries for BioAmp-EXG-Pill module
    * Added Footprint, Symbol and 3D files for Bio-Amp-EXG-pill Module
    [BioAmp-EXG-Pill.step]
2022-06-05 Added docsify content - pages and images for EOG, ECG, EEG, EMG (#21)
    * Rename filter makdown files
    The names for BioAmp EXG Pill filter code description markdown files has been changed to make it look more understandable for general public. The content will include information about the processing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
    * ECG images
    Containing Electrode placement for ECG, sample ECG data recorded using BioAmp EXG pill
    * ECG file updated
    Containing compressed jpg images.
    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
2023-04-27 Add v1.0 board graphics
2023-04-27 Update KiCad files v1.0
    [BioAmp-EXG-Pill.kicad_pcb, BioAmp-EXG-Pill.kicad_sch]
2023-05-16 Add BioAmp EXG Pill v1.0 graphics
    Add connection vectors, PCB images, basic circuit vector
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
